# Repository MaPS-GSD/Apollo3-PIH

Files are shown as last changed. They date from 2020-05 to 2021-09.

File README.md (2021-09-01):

# Apollo3-Patient Isolation Hood



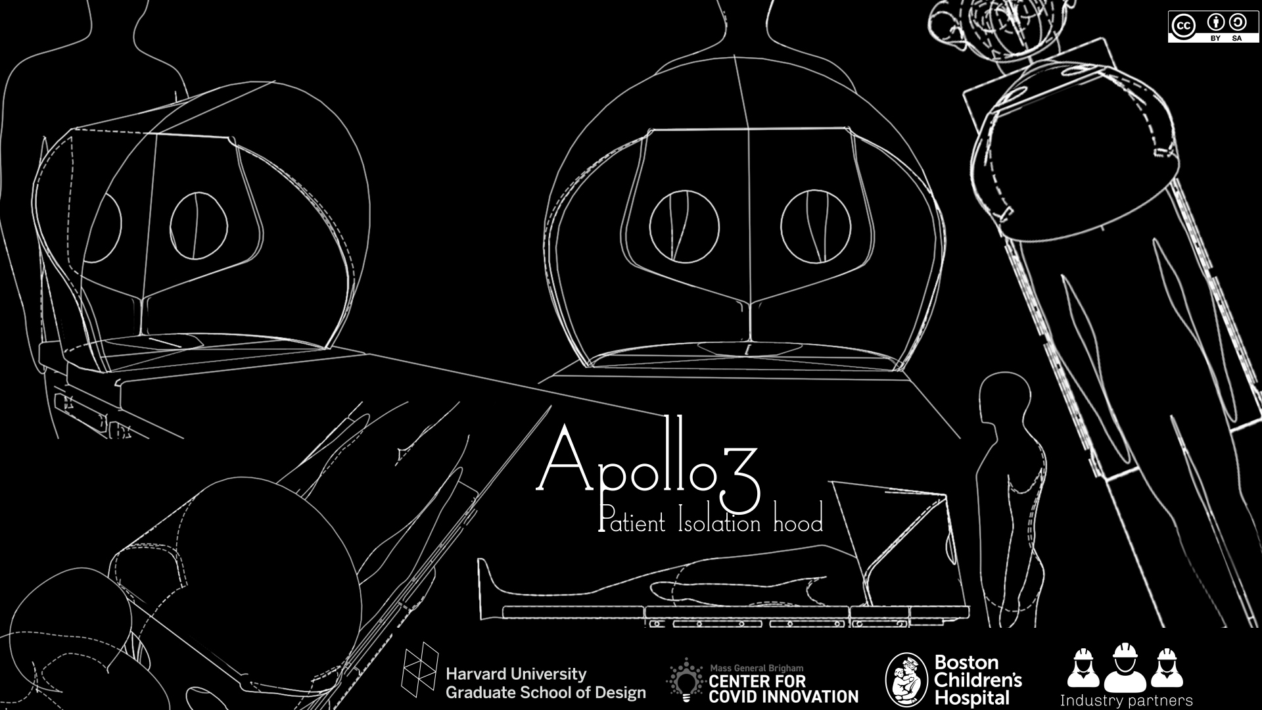
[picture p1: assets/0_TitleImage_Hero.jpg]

## General Information

**Category** : Labware + Devices

**Keywords** :Patient Isolation Hood, PIH, PPE

**Content of Package** :
- Apollo ReadMe (This) [**Print Ready**](README.pdf)
- Apollo3 Vector Cut File (.dxf) - [**Download HERE**](Dxf_cut_files/2020_05_05%20Apollo3_Cut%20File.dxf)
- Apollo Video:  [**Vimeo Link**](https://vimeo.com/415250896)

---
>**For questions, comments, issues and feedback email : [MaP+S Group](mailto:mapsgroup@gsd.harvard.edu?subject=[Apollo3-PIH])**
---

### Disclaimer
Please note: On Friday, May 1 the FDA issued an Emergency Use Authorization for Protective Barrier Enclosures.  The authorization provides specific guidance for manufacturing.  The Apollo PIH has not yet been evaluated with respect to these guidelines.  The letter and two associated fact sheets are available at [https://www.fda.gov/medical-devices/emergency-situations-medical-devices/emergency-use-authorizations#covid19ppe](https://www.fda.gov/medical-devices/emergency-situations-medical-devices/emergency-use-authorizations#covid19ppe).  

The product as a protective barrier enclosure, provides an extra layer of barrier protection in addition to PPE and is not meant to replace PPE.

Please also note: The Apollo PIH is under active development and refinement.  Please check this repository often for design modifications and additional information. 

The Apollo PIH has been tested by clinicians at Massachusetts General Hospital and Boston Children's Hospital, but there are many different regulations regarding medical devices so please follow local guidelines that apply to your region. Please note that safety is the primary objective. Medical equipment must be approved before it is distributed. This is possibly a matter of life or death. 

This work may be reproduced, modified, distributed, performed, and displayed for any purpose, but must acknowledge the Apollo PIH project. Copyright is retained and must be preserved. The work is provided as is; no warranty is provided, and users accept all liability.

### License
Except where otherwise noted, content on this project is licensed under a [Creative Commons Attribution-ShareAlike 4.0 International license](https://creativecommons.org/licenses/by-sa/4.0/). See [License](LICENSE.md).
***
## Project Overview

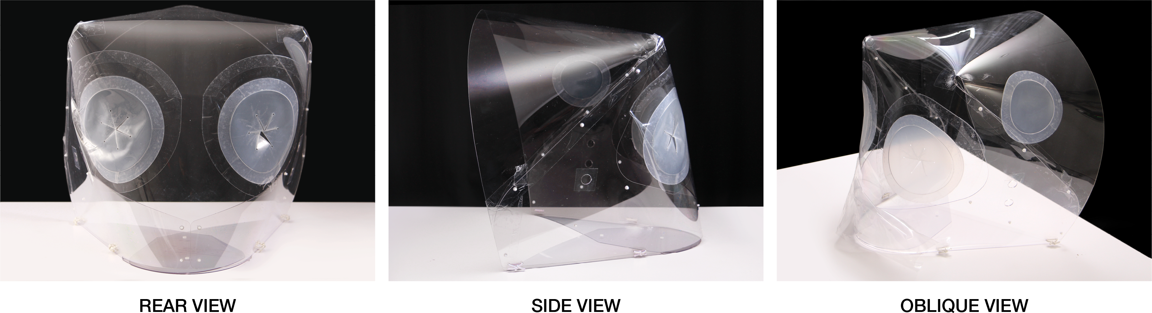
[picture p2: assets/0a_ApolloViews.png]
Apollo3 Patient Isolation Hood
> 

### Description
The Apollo Patient Isolation Hood (PIH) is a localized negative-pressure ventilation system for hospital beds to help contain the droplet spread of COVID-19, including during aerosol-generating medical procedures such as intubation and extubation. The PIH encloses a patient’s upper torso and head in a negative-pressure environment. It provides barrier protection between healthcare provider (HCP) and patient, and aerosol control via the negative pressure environment. The hood may also contain the spread of the virus from less critically-ill patients, reducing the need for invasive procedures.

The versatility of the Apollo PIH means that it can be used in any care setting (OR, PACU, ICU, ED, EMS) and can be rapidly secured to a variety of beds.  The lightweight (<5 lbs) design allows for ease of assembly, use, and disposal. The primary structure is composed of a single flat sheet of PETG plastic that is assembled into a 3-dimensional form, minimizing the number of seams for optimal viewing clarity.  Flexible sealed armports provide HCP access to patients.  A minimal amount of folds and seams in the primary enclosure provide optimal viewing clarity.  

### Design Concept
The primary design goal of the hood was to enclose the patient’s torso and head without restricting HCP ability to provide care or inducing claustrophobia in patients. The enclosure of the Apollo PIH derives its form and rigidity through the principle of active bending, a structural behavior achieved by the elastic deformation of initially flat elements. The main intention was to leverage this structural principle to create a stable, rapidly deployable 3D form that can be fabricated from readily available sheet materials using minimal joinery.

### Key Features
The primary design element of the Apollo PIH is the enclosure - a thin sheet of clear PET-G plastic in 60mil (approximately 1/16”) thickness.  The enclosure can be CNC cut from a flat sheet of PET-G  measuring a minimum of 48” x 72”.  The Apollo PIH enclosure measures approximately 22” in width, 23” in height and 22” in depth and is approximately 0.15 m3 in volume.

> Apollo3 Patient Isolation Hood

Several key features of the prototype are outlined below:
- (2) arm ports at the rear of the PIH provide healthcare provider (HCP) access to the patient. - An additional auxiliary port on one side of the PIH allows for additional patient access as needed.
- Minimal surface seams allow for an unobstructed view of patient.
- Adaptable attachment mechanism allows for use on a variety of bed types (OR, ICU, etc.)
- Side arms provide a double thickness at the base of the PIH for stability and structure
- Various suction ports accept common negative pressure hoses, including a ⅞” diameter (common in OR) as well as smaller 3/16” ID tubing (common in the ICU).  
***
 ### Flow and Pressure Testing - 👨‍⚕MGB
  Work in Progress
  Negative Pressure Hood Working:-  [YouTube Link](https://youtu.be/yTqlieDpH2M)
  ***

## Production Details
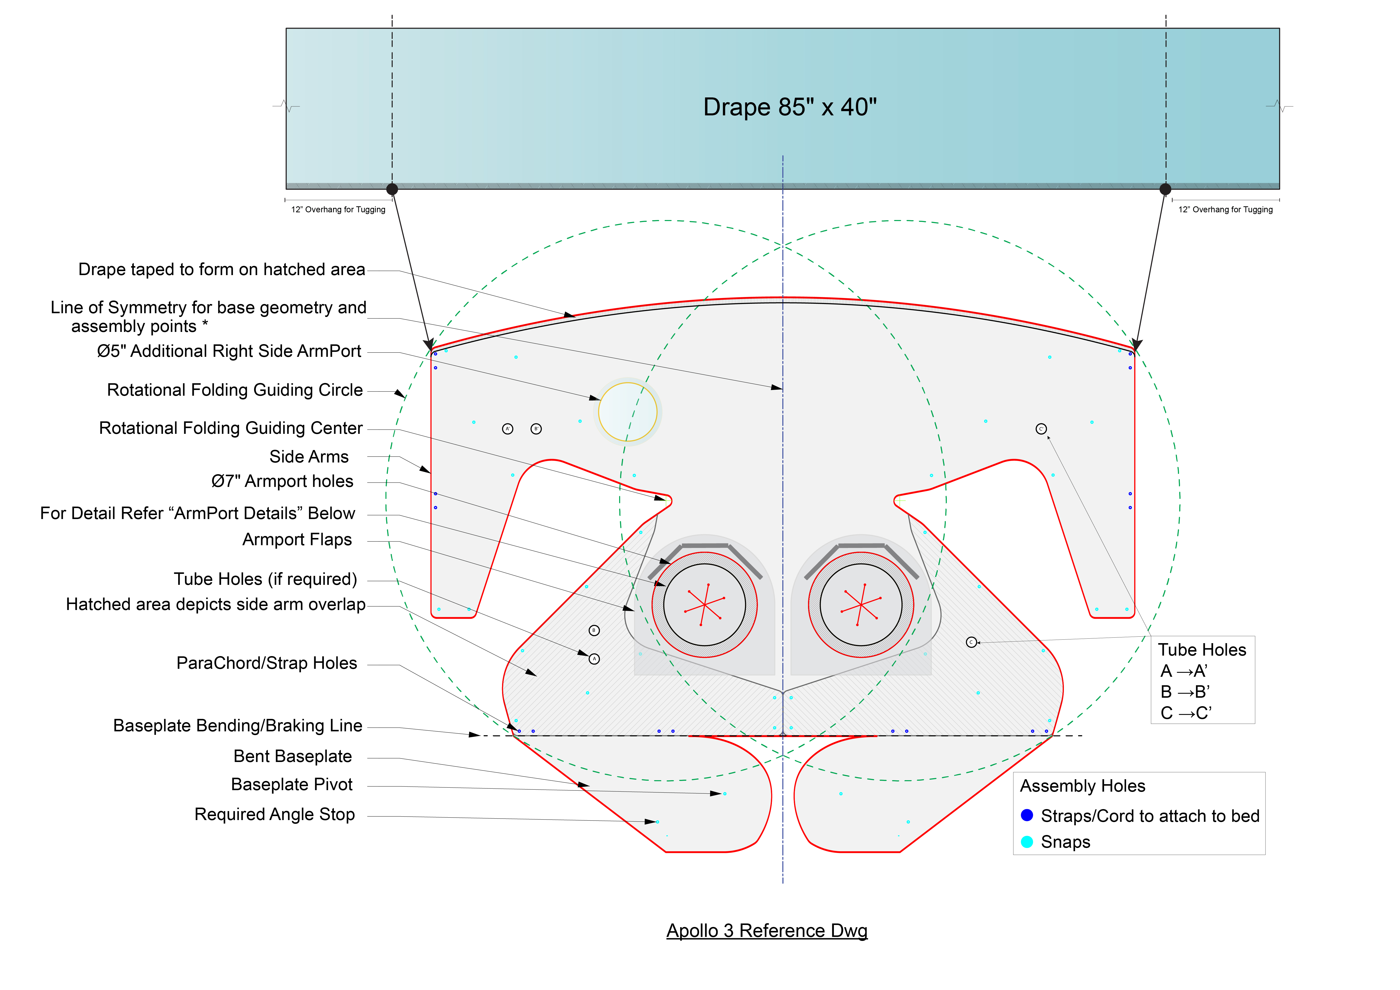
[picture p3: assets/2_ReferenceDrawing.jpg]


### Bill of Materials

Item Description  | Dimensions( in or sqrIn) | Quantity | Link | Notes
|------------- | ------ | -------------| -------------| -------------|
 3/16" bungee cord | 12" | 2 |[Amazon](https://www.amazon.com/T-W-Evans-Cordage-SC-316-100-100-Feet/dp/B00DKA4VQG/ref=sr_1_3?dchild=1&keywords=white+bungee+cord+3%2F16%22&qid=1587383739&s=sporting-goods&sr=1-3-catcorr)
 Velcro cord management strap  | n/a | 2 | [Amazon](https://www.amazon.com/Pasow-Reusable-Fastening-Adjustable-Management/dp/B01CFKQYAW/ref=sr_1_4?dchild=1&keywords=cord+management+velcro+white&qid=1587394037&sr=8-4)
 Adjustment Hook  | n/a | 2 | [Amazon](https://www.homedepot.com/p/ProGrip-Better-Than-Bungee-6-ft-100-lbs-Break-Strength-Particle-Rope-Lock-Paracord-055160/206957471?modalType=drawer)
 Push-In Rivet  | n/a | 17 | [McMaster-Carr](https://www.mcmaster.com/90136a574)
 Button Snaps  | n/a | 1 |  [McMaster-Carr](https://www.mcmaster.com/95691a660) | *1*
 Drape tape / seam tape (must be low surface energy tape)  | 61" | 1 | [HomeDepot](https://www.homedepot.com/p/Gorilla-1-5-in-x-5-yds-Crystal-Clear-Tape-5-Pack-6015002/205493971?mtc=Shopping-B-F_D24-G-D24-Multi-Multi-NA-Feed-PLA-NA-NA-All_Paint&cm_mmc=Shopping-B-F_D24-G-D24-Multi-Multi-NA-Feed-PLA-NA-NA-All_Paint-71700000032325895-58700003835893718-92700030694006321&gclid=CjwKCAjwkPX0BRBKEiwA7THxiJXWI0-JAcbqYryMsjvaev1nBxPw_FWMW1czSJxp9qHvZyLyDKl_yhoCxfgQAvD_BwE&gclsrc=aw.ds) | *2*
 LDPE film (2mil)  | 40" | 1 | [Uline](https://www.uline.com/Product/Detail/S-5445/Plastic-Sheeting/Clear-Poly-Sheeting-2-Mil-8-x-200) 
 1/16" PET-G sheet | 72x48" | 1 | n/a
 Tpu film for port holes (2-5mil)  | 13" X 13"| 2 | n/a
 Tpu film for port hole flaps (2-5mil) | 13" x 13" | 2 | n/a
 Adhesive sheet for attaching handports | 13" x 13" | 4 | [Laminator.com](https://www.laminator.com/51-x-150ft-optically-clear-double-sided-mounting-adhesive-permanent-permanent.html)
 Colored vinyl stickers for intuitive assembly and risk warning | n/a | 4 | [Overnightprints.com](https://www.overnightprints.com/stickers)
 95 gallon clear trash bag for disposal | n/a | 1 | [Uline](https://www.uline.com/Product/Detail/S-15540/Trash-Liners-Bags/Uline-Trash-Liners-95-Gallon-25-Mil-Clear?pricode=WB0503&gadtype=pla&id=S-15540&gclid=Cj0KCQjwhZr1BRCLARIsALjRVQOMShqprypOodH6yqqy-GNPSxb2Hep2NU1SgADXMQsUt7F44VXUqlQaAiDwEALw_wcB&gclsrc=aw.ds)
 Instruction Sheet | n/a | 1 
 1 gallon ziploc to hold instructions and cords | n/a 
---
*1. The button snap used for locking the fixing the position of the baseplate can be replaced by a push-in rivet if needed.*

*2. Must be low-surface-energy tape.*

---
### Recommended Production Guidelines

#### A) Enclosure
#### 1. Cutting
The Apollo PIH requires a minimum stock size of 72” x 48”. The stock can be cut using a number of CNC processes including a knife cutter, laser cutter, or router.  In the case of a CNC router, a ⅛” diameter endmill is required to successfully cut small interior features.  A list of suggested cut settings are provided below.  Please keep in mind that these settings are specific to the machines listed and will likely need to be modified for other scenarios. 
- Knife Cutter ([Zund G3M2500](https://www.zund.com/en/cutting-systems/digital-cutting-systems/g3-cutter))
  - Bed Size: 98” x 52”
  - Tool: Universal Cutting Tool (UCT) with [glide shoe](https://shop.zund.us/en-us/products/alle-produkte/cutting-accessories/gliding-shoe))
  - Blade: Type6 blade
  - Depth: 0.02” per pass
  - Speed : 6” per second 
  - Total Time : ~ 18 minutes.
- Laser Cutter (*450 Watt Multicam Magnus 48x96 CNC Laser, 4” Focal Lens*)
  - Speed: 480 IPM
  - Power 60%
  - Frequency: 10,000 PPI

#### 2. Base-Plate Braking/Bending
 
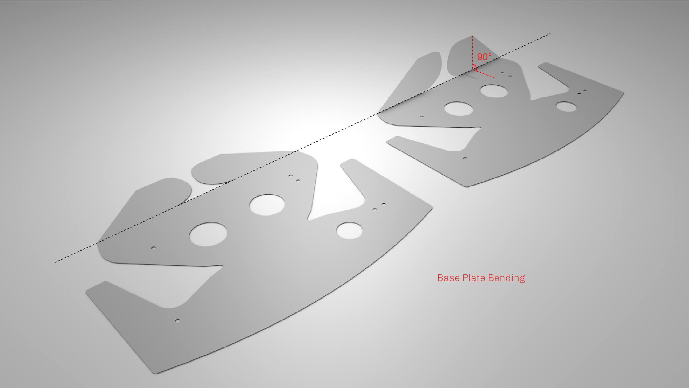
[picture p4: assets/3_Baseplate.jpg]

*Caution : Do not score the material before bending/braking* 

The baseplate portion of the Apollo PIH enclosure must be cold-formed to a 90 degree angle relative to the rest of the enclosure prior to assembly.  To date, this has been successfully accomplished on a sheet metal finger brake such as the Baileigh SBR-4020 shear brake roll ([Link](https://www.baileigh.com/shear-brake-roll-sbr-4020)).
Additional forming processes such as the use of a line brake or heat gun, or design modifications to the enclosure such as eliminating the base plate or incorporating a secondary hinge mechanism, exist as potential alternatives though they have not been tested by the design team. 

#### 3. Push-in Rivets
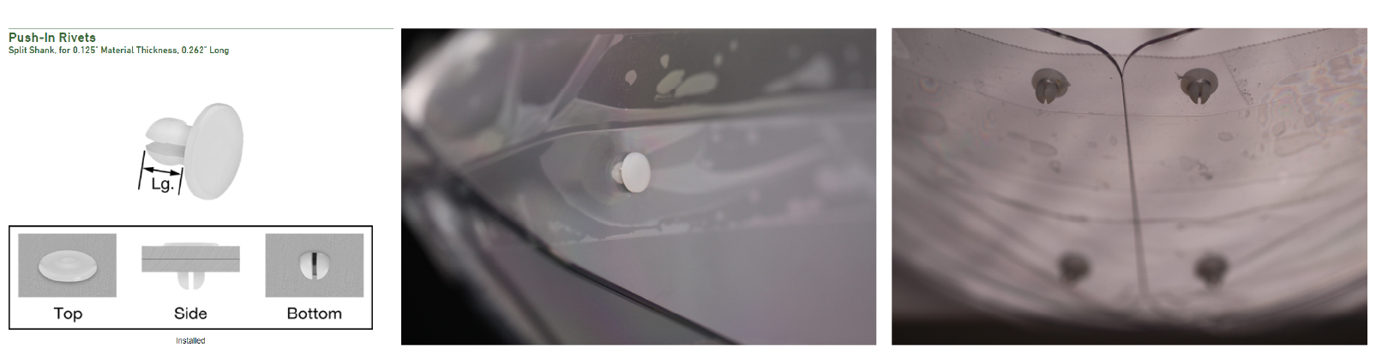
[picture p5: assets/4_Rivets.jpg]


Push-in plastic rivets were selected as the preferred fastener, as they were simple to use and had no sharp edges that could catch on to clothing, medical instruments etc. 3/16” holes in the main enclosure facilitate the riveting and was done by hand. 16 rivets are needed (8 per side of symmetry) for maintaining the shape of the Apollo while 2 rivets (or 1 rivet & a button snap)are needed for the baseplate ( 1 to pivot (*red*) and 1 to lock (*blue*)).
<p align="center">
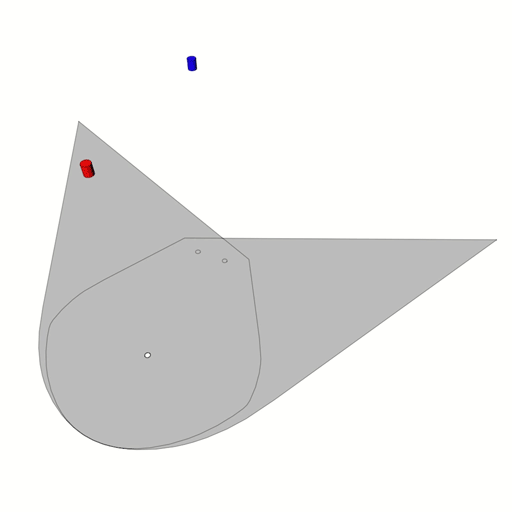
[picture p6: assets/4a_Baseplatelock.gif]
  
</p>

*The width of the Apollo can be adjusted by adjusting the location of the pivot and the lock.Multiple perforations can be added to have it adapt to a range of widths.*

#### B) ArmPorts + Auxiliary Ports

 <p align="center">
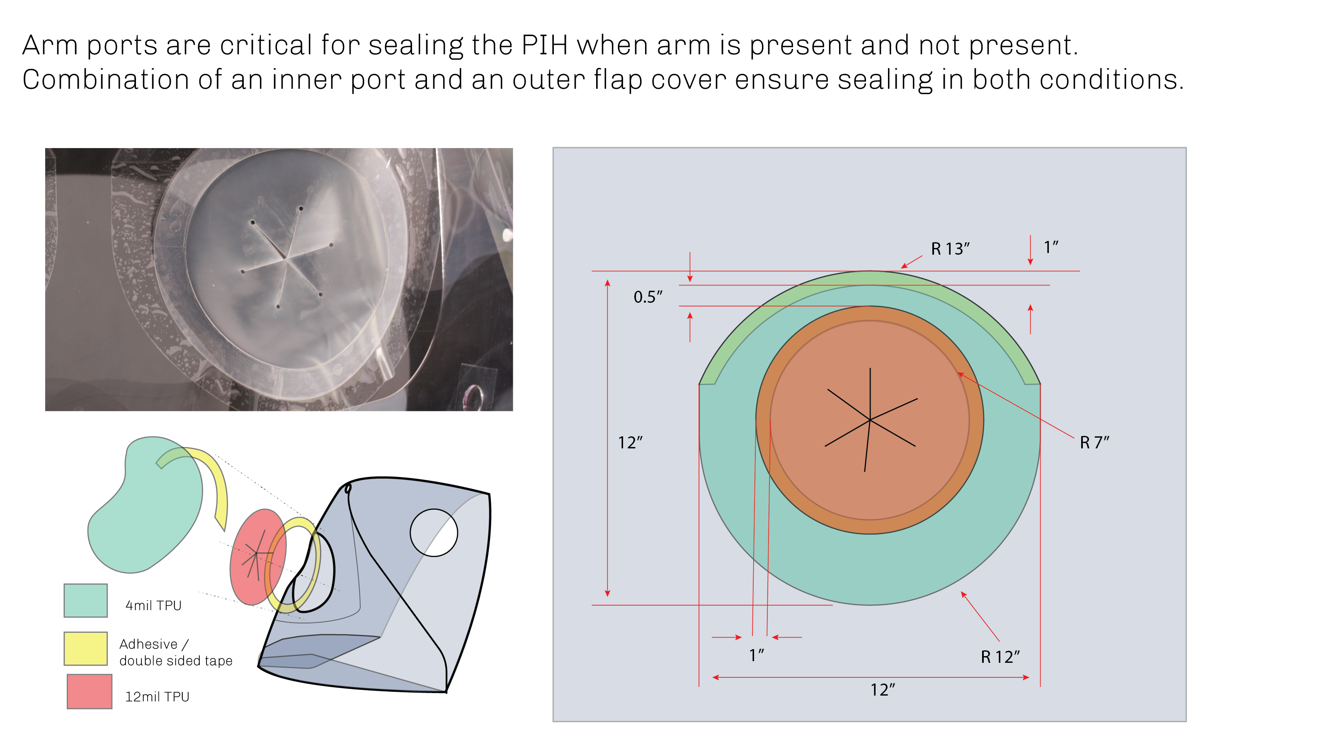
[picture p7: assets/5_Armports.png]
  
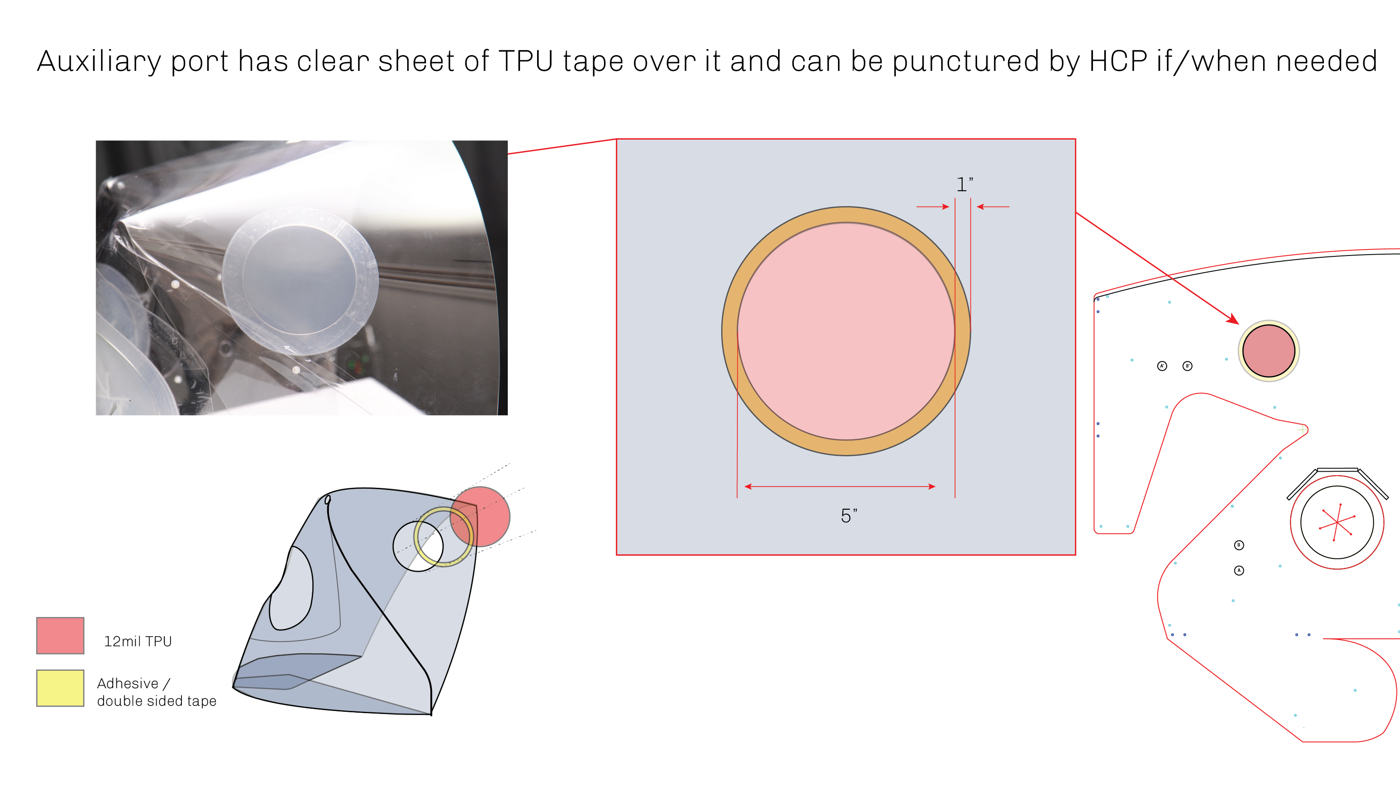
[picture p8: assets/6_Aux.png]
  
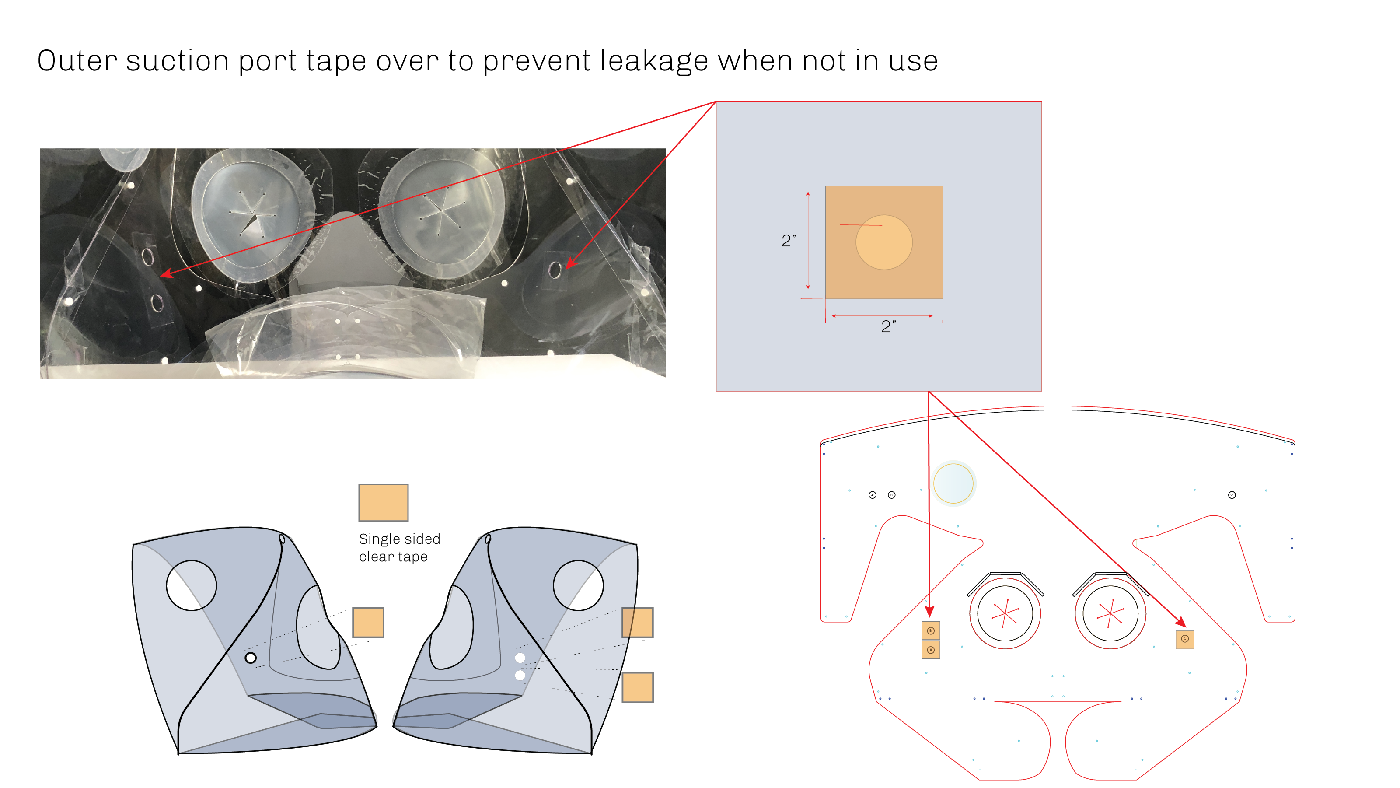
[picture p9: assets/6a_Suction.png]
  
</p>

Each arm and auxiliary port on the Apollo PIH is composed of three primary components - a laser-cut 5 mil TPU portal, a clear, double-sided adhesive film, and a port cover.  

- TPU Portal: Laser cut from 5 mil TPU.  The portal is an inverted “mercedes” design, with circular relief holes at the tip of each cut to minimize the potential for tearing.  It can be CNC cut on a laser cutter or a knife cutting machine such as a ZUND.
- Adhesive Ring: The adhesive ring can be cut from a sheet of adhesive film.  
- The port cover/flap 

#### C) Bed attachment mechanism
<p align="center">
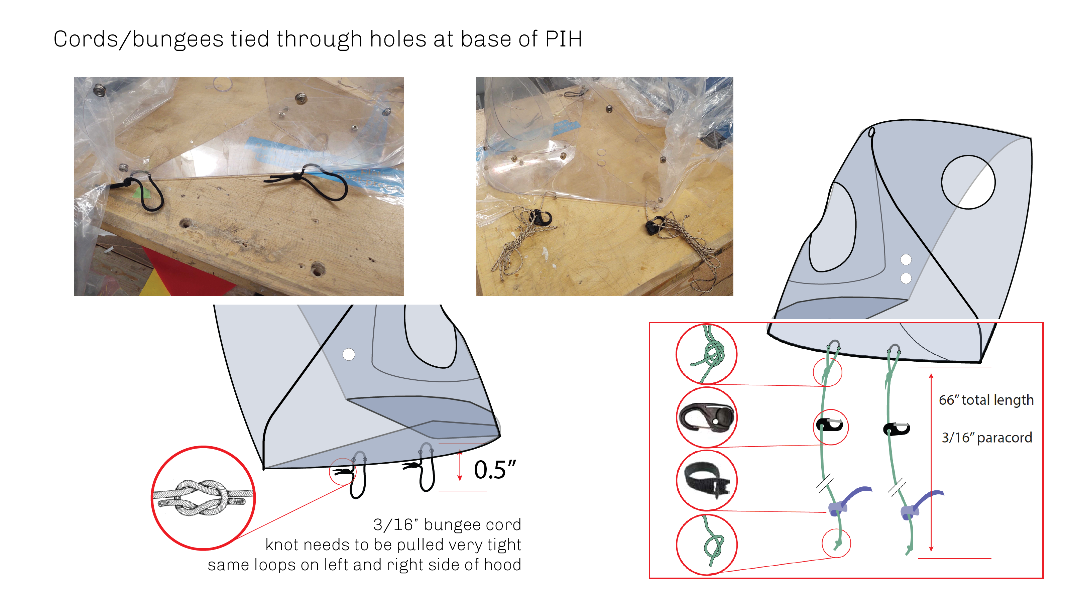
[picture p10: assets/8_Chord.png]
  
</p>

Perforations are located on the base perimeter (dark blue in _Reference drawing_) of the back plate to enable the use of cords/straps in order to attach the Apollo to different sized beds.

#### D) Drape
<p align="center">
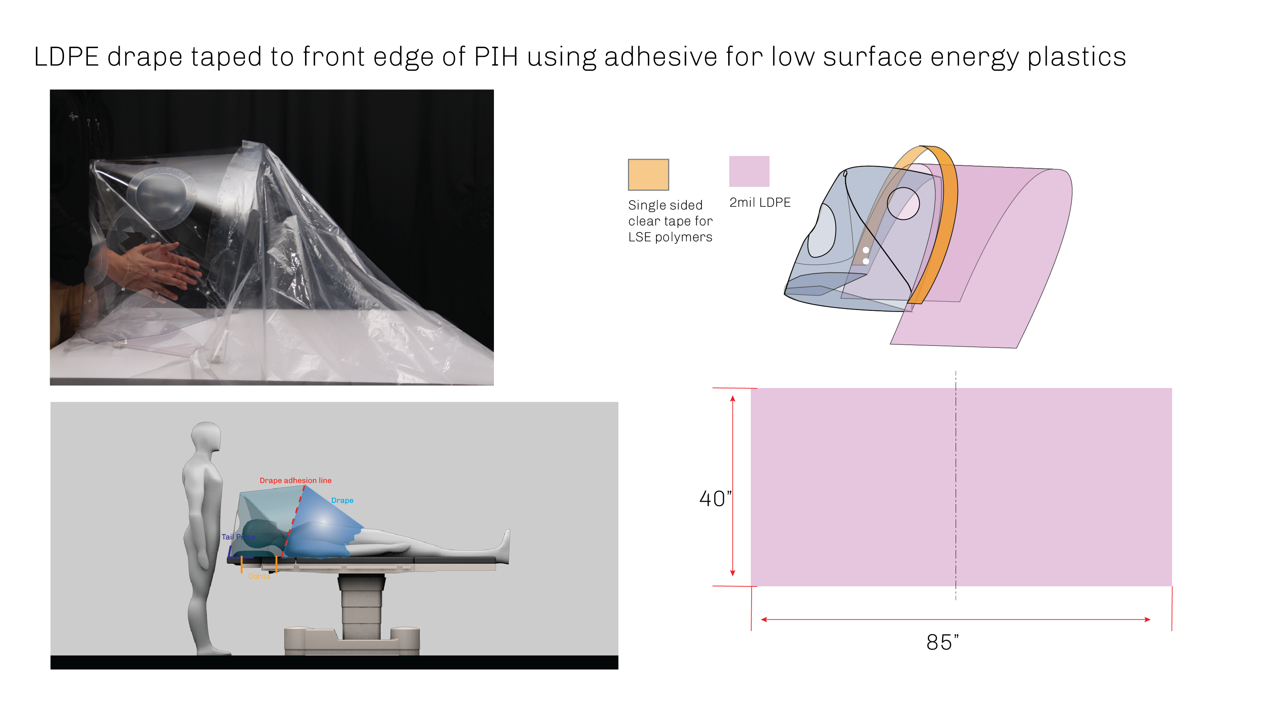
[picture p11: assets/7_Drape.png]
  
</p>

The drape is a rectangular piece of LDPE with dimensions 85” x 40” . Refer to the reference drawing and assembly instructions for details. A 12” offset has been left on both ends to facilitate tucking under the patient to get a good seal. 

#### E) Tail Piece
<p align="center">
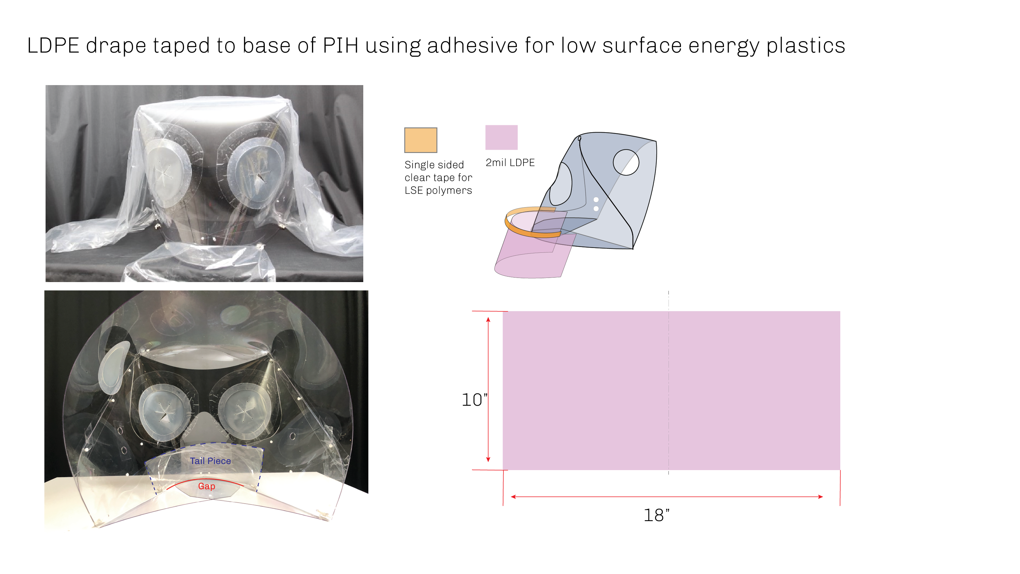
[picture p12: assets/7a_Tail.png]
  
</p> 
A small sheet of LDPE (Same as Drape) is stuck on the back plate and tucked under the baseplate to cover the gap between the baseplate and the back wall to maintain the seal.

### Assembly
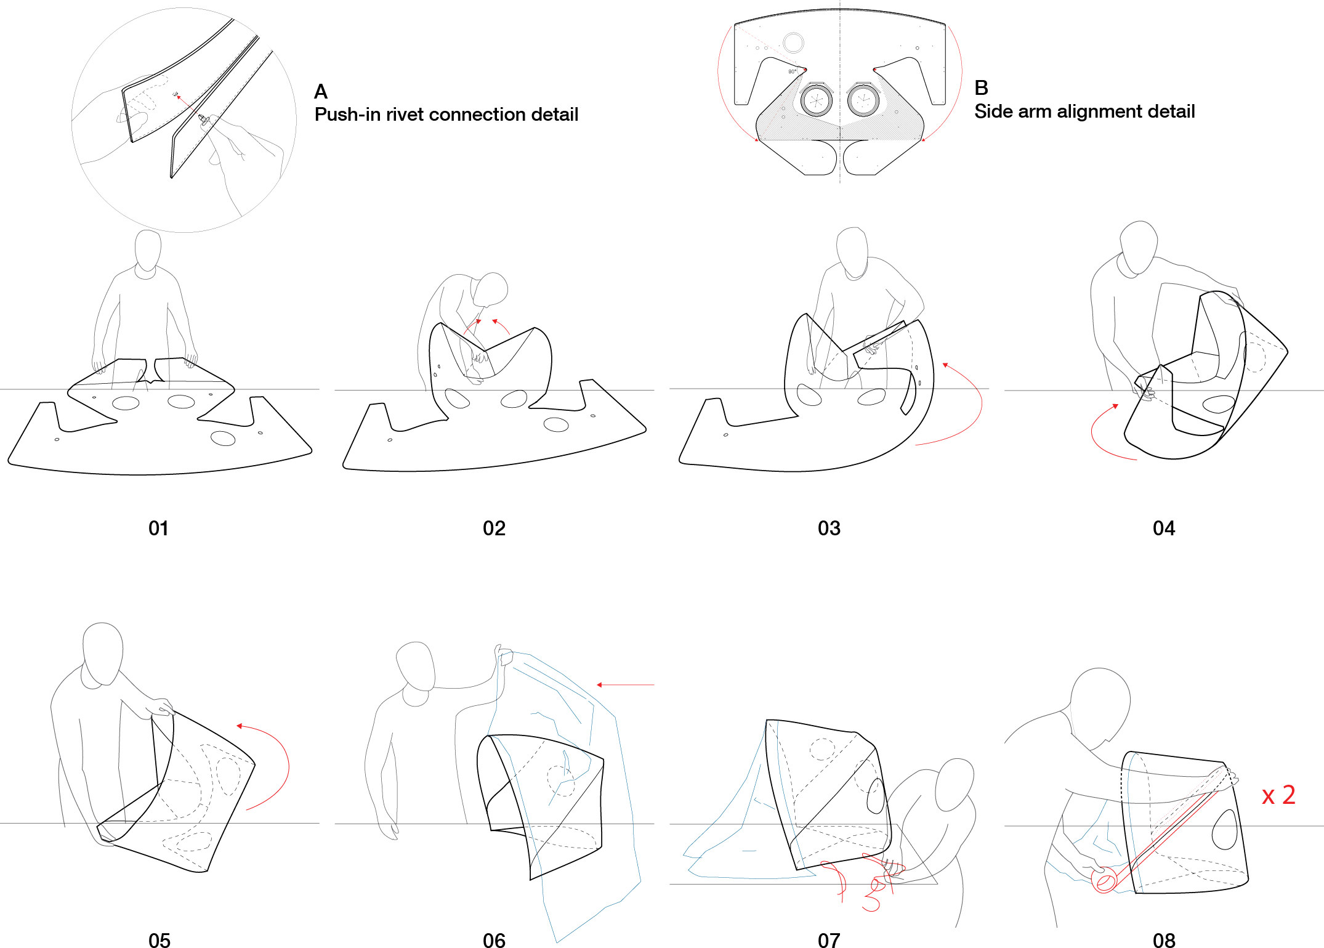
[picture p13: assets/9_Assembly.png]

> 
- Step 01: Place Apollo PIH enclosure on a flat surface with the folded baseplate facing upwards.  
- Step 02: Fasten the opposing sides of the baseplate together using two push-in rivets located on the baseplate.  See detail A for connection detail.  
- Step 03: Fold one side arm toward the interior of the enclosure.  Fasten to the main portion of the enclosure using (8) push-in rivets. 
- Step 04: Repeat Step 03 for the opposite side arm.
- Step 05: Place the Apollo PIH upright so that the baseplate is resting on a horizontal surface. 
- Step 06: Attach the plastic drape to the front edge of the Apollo PIH using double-sided tape.
- Step 07: Fasten the provided straps to one side of the Apollo PIH.
- Step 08: Adhere clear tape over the external seams of the Apollo PIH (one per side), taking care to completely cover the seam. 

### Alternate Details
Below are some alternative details we have experimented with towards the end goal as design variants but these are yet to be tested clinically.

- **Material**

    While the Apollo PIH is designed to be fabricated from PET-G measuring 60mil (~1/16”) in thickness, though early prototypes fabricated from thinner, 30mil (~1/32”) were also sufficiently rigid. 

- **Form**

    Following alternatives have not been checked thoroughly in a clinical setting  and have only been provided as suggestions.

  - Apollo 1 Main Feature:
    - Use of Tabs and Slots instead of hardware
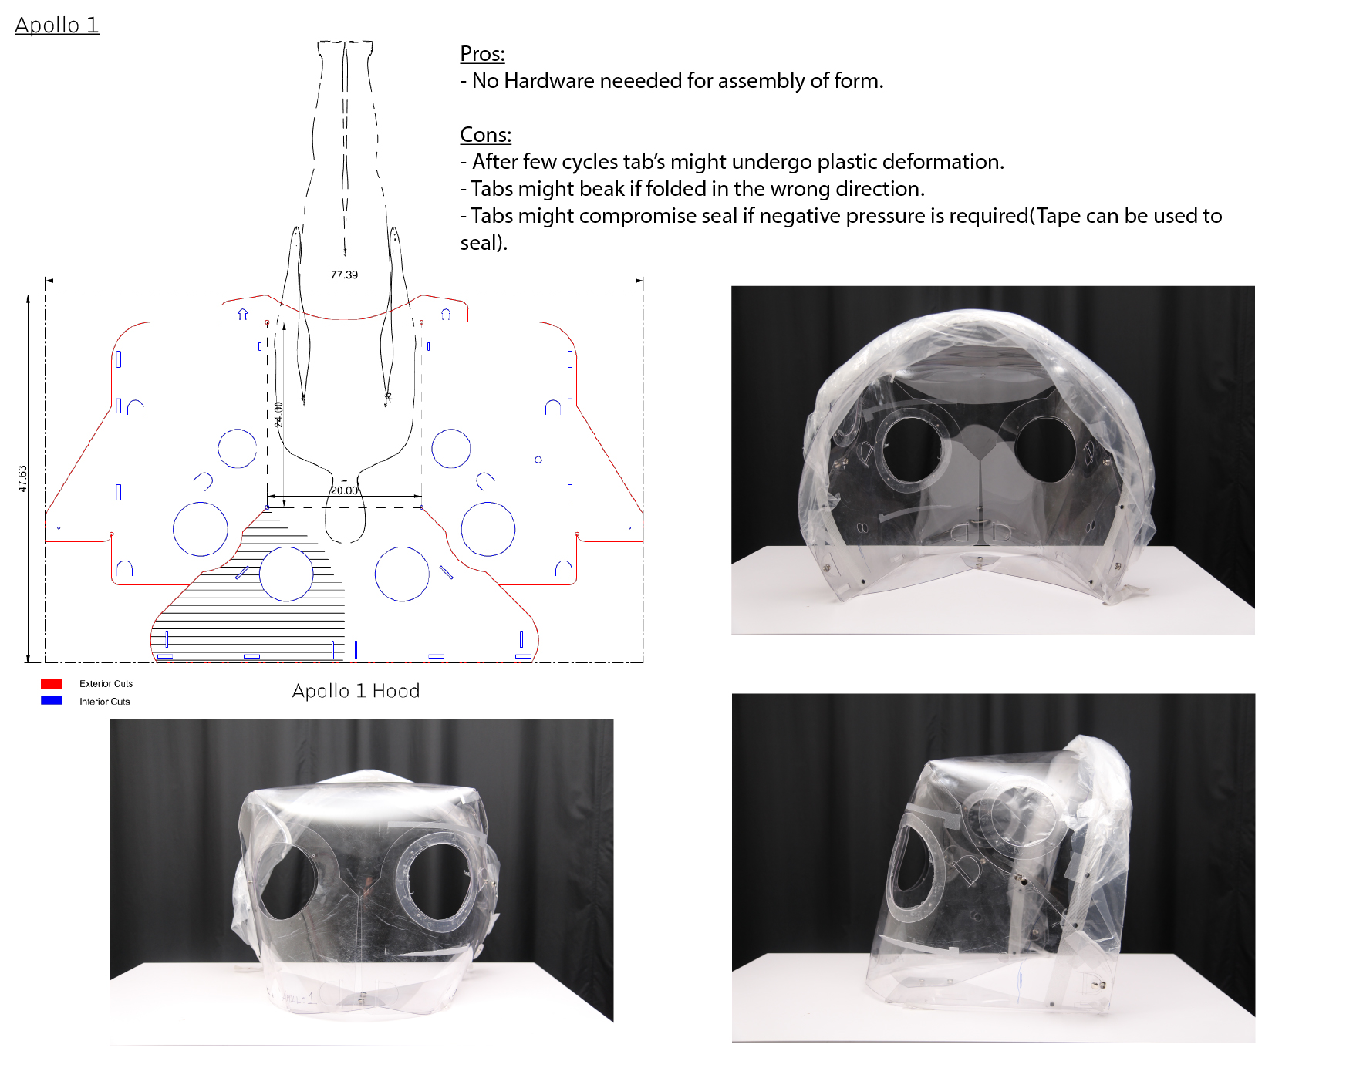
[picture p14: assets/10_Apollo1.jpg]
Apollo3 Patient Isolation Hood
    

  - Apollo 1.5_Minimal Main Feature:
    - Reduction of overlap and material.
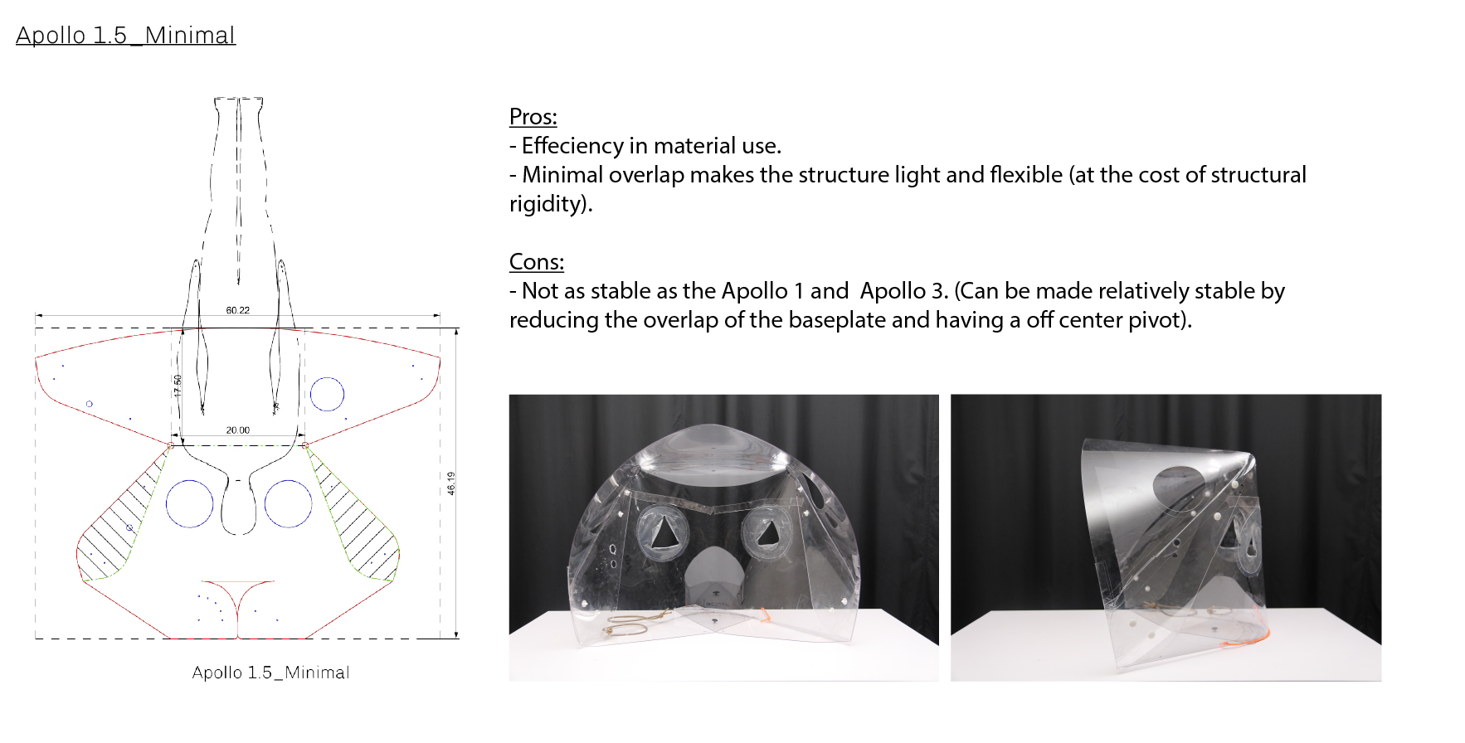
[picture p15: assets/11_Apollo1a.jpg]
Apollo3 Patient Isolation Hood
    

- **Arm Ports**
 
    <p align="center">
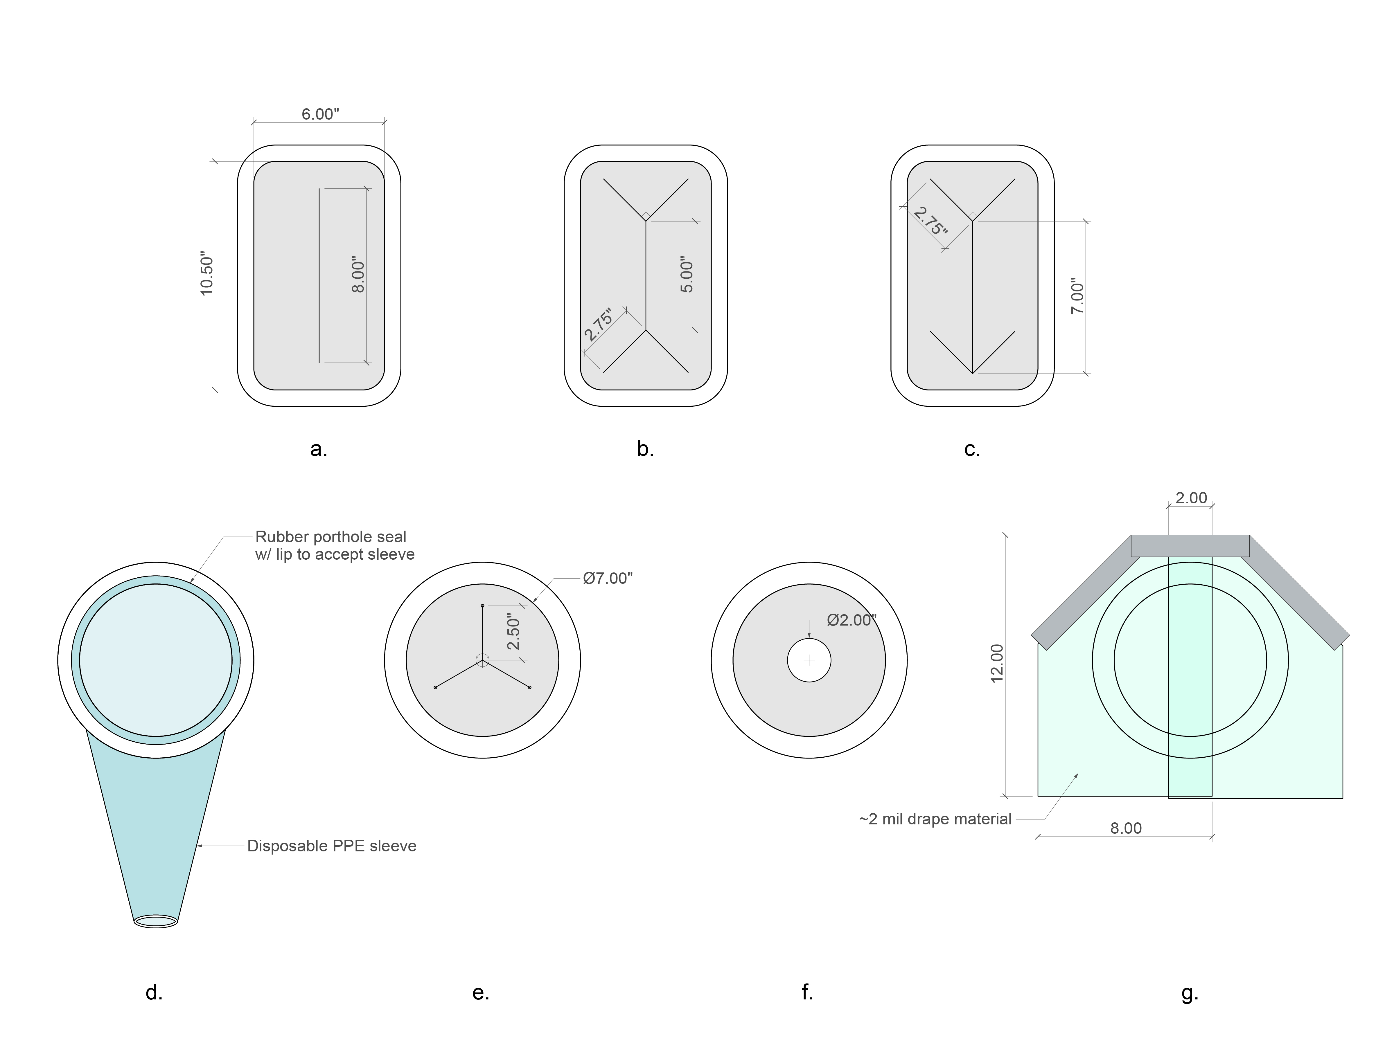
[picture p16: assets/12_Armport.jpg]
    
    </p>

Multiple iterations of the armport design were undertaken with various materials and can be found in the diagram above. 
- Versions a and f Require a thinner gauge or extensible material as they can otherwise restrict arm movements while in use. Version f also requires a secondary drape taped over the opening to maintain a seal
- Versions b, c, and e work well with the specified 5+mil TPU and 1/16” silicone sheets (available on McMaster Carr). They feature a self-closing design and when used with the silicone sheets may not require a covering drape. Version c is best for thinner materials that lack the stiffness to hold their shape overwise
- Version d makes use of disposable PPE sleeves widely available in many material types. The sleeve is stretched around a rubber porthole seal (such as [this product).
- Version g simply uses two pieces of the drape material with an overlap to help limit air escape when in use.
- Clear PVC sheets were experimented with in both 0.08” and 0.04” thicknesses but were found to be too stiff to work properly and often grabbed at the sleeves and gloves when in use. 

## Documentation
>Evolution
<p align="center">
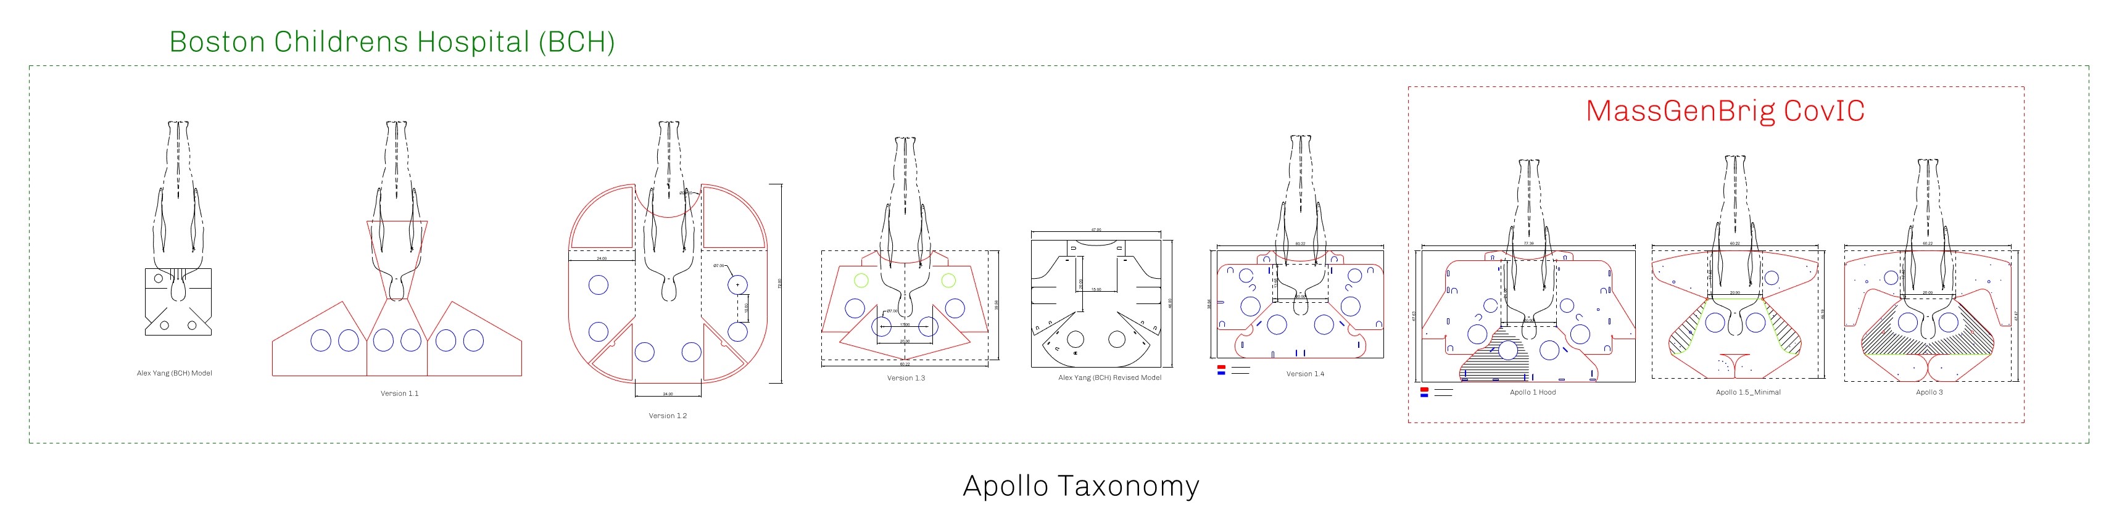
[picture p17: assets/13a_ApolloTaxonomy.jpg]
    
    </p>
    
>Apollo3
<p align="center">
    
    </p>

>Apollo3 Clinical Testing
<p align="center">
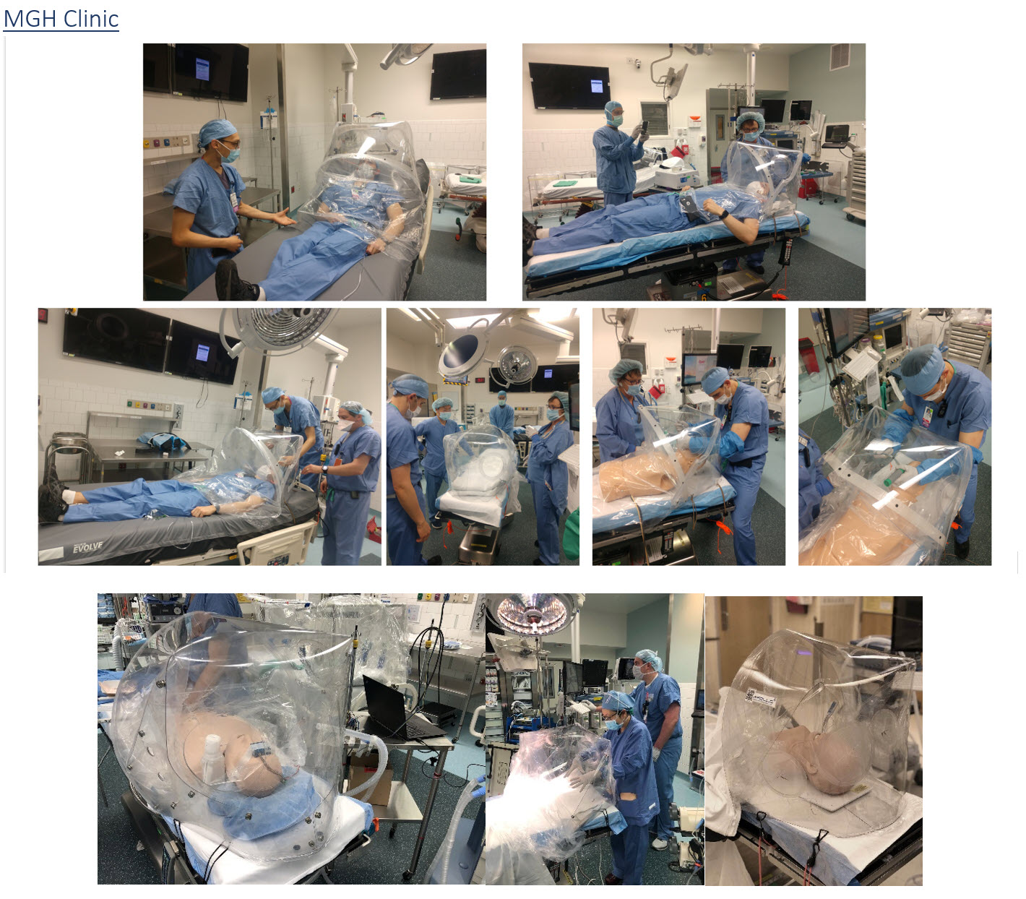
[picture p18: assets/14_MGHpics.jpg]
    
    </p>

## Update - 2021_08_31 - Apollo 4 - Production Model by Nathan Phipps
- Description:
Apollo 4 includes several modifications for manufacturing efficiencies as well as continued requests from clinicians. Clinical updates include an extra set of hand ports for accessing patients, removal of the TPU auxiliary port located on the upper right (clinicians view) of the unit, and addition of elliptical suction ports to allow for cylindrical suction tubes entering at a steep angle into the hood. The main alteration for manufacturability was modified PETG body shape which could allow for two units to be cut out of a single 4'x8' sheet, thus increasing yield in production. This new shape was created by removing the "wings", which offered increased stability and stiffness and instead broadening the base of the unit to increase stability. Apollo Medical Solutions, a company started by Nate Phipps and Chris Tolles was formed to facilitate production and distribution of the Apollo 4; the device was produced by H. Loeb Corporation of New Bedford, MA and purchased for testing by Massachusetts General Hospital. 

- Apollo4  Assembly Instructions [**Print Ready**](apollo3_productionModel_instructionsForAssembly.pdf)
- Apollo4 Vector Cut File (.dxf) - [**Download HERE**](apollo3_productionModel_mainBody_twoPer4x8Sheet.dxf)
- Apollo4 BOQ (.xlsx) - [**Download HERE**](apollo3_productionModel_BOM.xlsx)

<p float="left">

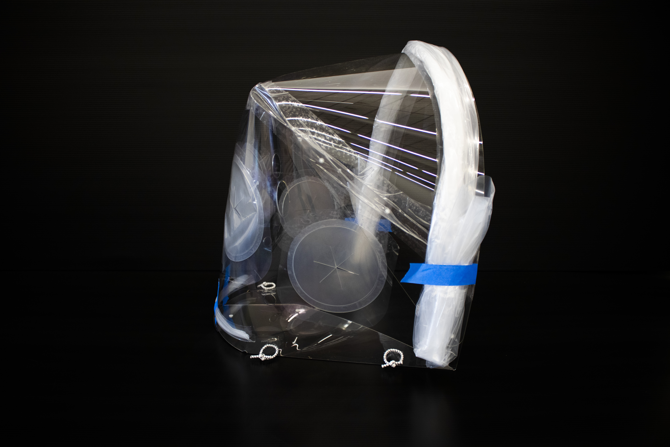
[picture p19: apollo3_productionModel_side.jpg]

</p>
<p float="left">

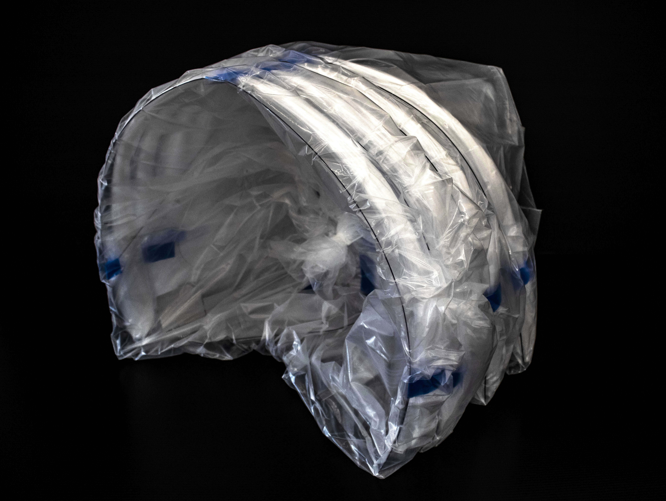
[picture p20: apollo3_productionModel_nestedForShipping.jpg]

</p>
<p float="left">
  
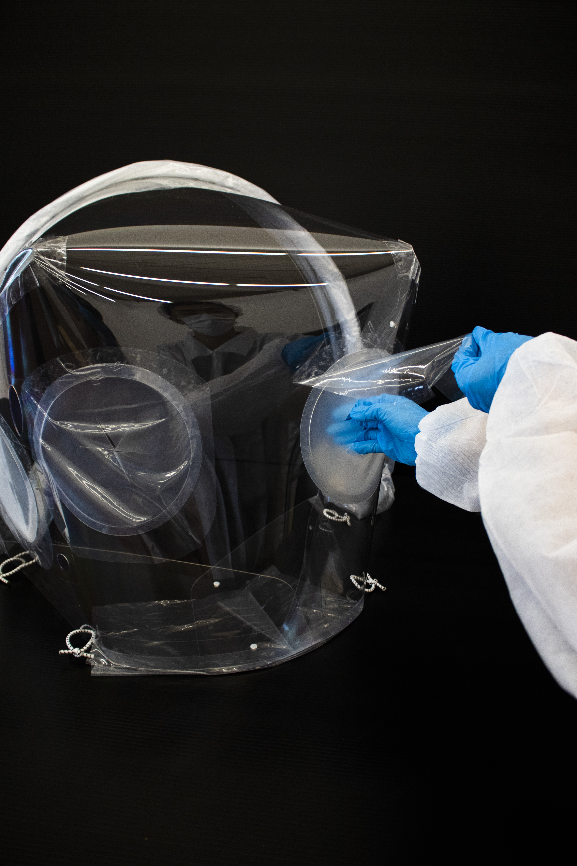
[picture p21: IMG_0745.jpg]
   
</p>
<p float="left">
  
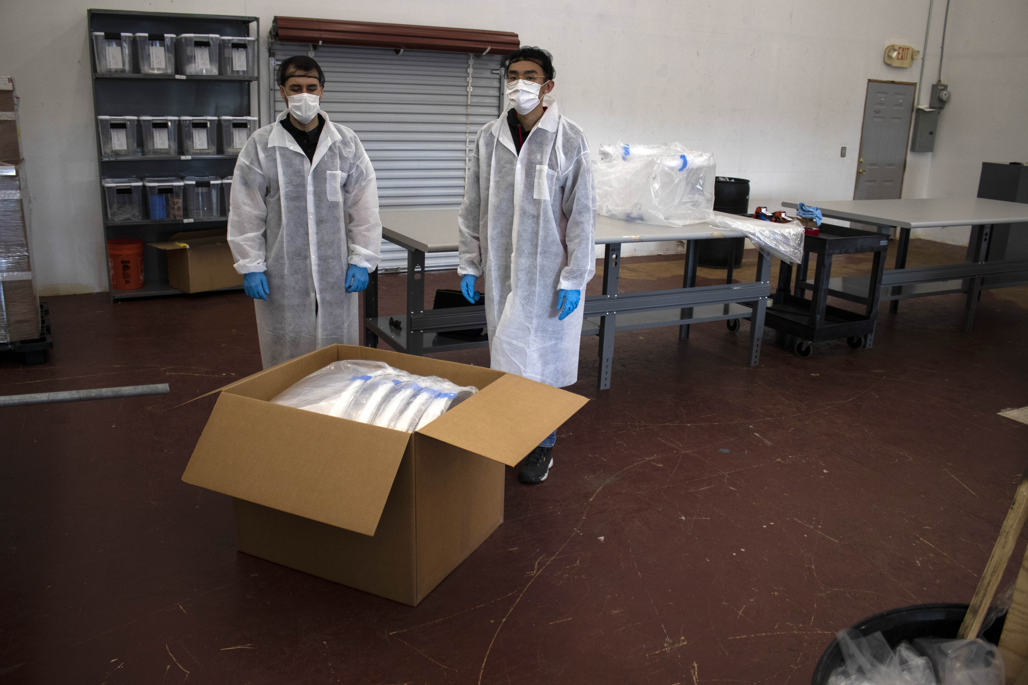
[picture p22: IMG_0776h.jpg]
   
</p>

## Attribution 

Attribution Report 
- **PIH Dimensions:** 
MGB Group + Boston Children’s Hospital
- **Form/Concept:**
Saurabh Mhatre, Christopher Hansen, Nathan Phipps, Eric Howeler, Samuel Smith, MD, 
- **Arm Ports
Design:** Daniel Tish, Daniel Castello, Christopher Hansen, Jonathan Grinham, 
- **Clinical Input:** Samuel Smith, MD; 
- **Base Structure/Attachment Mechanism:**
Nathan Phipps, 
- **Drape:**
Nathan Phipps, Chris Hansen, 

## Acknowledgements
- Several clinicians provided key clinical feedback that drove design decisions, from MGH Anesthesia: Samuel Smith, MD, MPH; JP Wang, MD, PhD; Michelle Szabo, MD; Scott Streckenbach, MD; Alex Kuo, MD; Kendrick Shaw, MD, PhD; Angela Dai; Matt Vanneman, MD; Celeste Day.  From MGH Pediatrics, Kris Olson.  From the MGB Center for COVID Innovation; Li Li, PhD; Aditya Kumar; and Gary Tearney, MD, PHD.  
- Chris Hansen, Digital Fabrication Technical Specialist at the Harvard GSD;  Eric Howeler, Associate Professor of Architecture at the GSD; Saurabh Mhatre, Research Associate at the Harvard GSD & Harvard CGBC; and Nathan Phipps, played key roles in refining, prototyping, and coordinating fabrication of the Apollo 3 design. Zach Seibold, Jonathan Grinham, Daniel Tish, Daniel Castello and Ryan Pierce participated in design iteration and early prototyping.  
- James Weaver, Senior Research Scientist at the Wyss, facilitated the initial collaboration and has been instrumental in sourcing materials. 
- The Boston Children’s Hospital Surgical Innovation Fellowship team, including Heung Bae Kim, MD; Farokh Demehri, MD; Robert Crum, MD; Kyle Wu, MD; Brianna Slatnick, MD; and Alex Yang, BS, helped to develop the first versions of the Apollo design and provided clinical input throughout the design process.
- Initial design prototypes were produced with the help of PolyFab, and Roger Diebold (CEO, Solchroma Technologies) along with H. Loeb Corporation.

A full attribution list is as follows
Aaron Ross,
Adam Smith,
Aditya Kumar,
Alex Kobald,
Alex Yang,
Alexander Kuo,
Angela Dai,
Brianna Slatnick,
Celeste Day,
Chris Hansen,
Chris White,
Daniel Castelo,
Daniel Tish,
David Concha,
David Hamm,
David Wallace,
Eric Howeler,
Euan Mowat,
Farokh Demehri,
Fernanda Sakamoto,
Heung Bae Kim,
James Weaver,
Jonathan Grinham,
Jonathan Langer,
Koushik Garapti,
Kristian Olson,
Kyle Wu,
Lara Tomholt,
Martin Bechthold,
Mehra Golshan,
Michael Sherman,
Michele Szabo,
Norman Wen,
Robert Crum,
Ryan Pierce,
Sam Smith,
Saurabh Mhatre,
Ted Ngai,
Ted Sirota,
Zach Seibold.

## References

### Press
- Harvard GSD Press Release [Link](https://www.gsd.harvard.edu/2020/05/gsd-participates-in-global-open-source-effort-to-develop-patient-isolation-hoods-for-boston-hospitals/)
- Selected Articles
    - https://news.harvard.edu/gazette/story/2020/04/graduate-school-of-design-begins-ppe-production-for-area-hospitals/                                                 
    - https://www.architecturalrecord.com/articles/14570-architects-and-engineers-help-develop-isolation-hood-for-covid-19-patients     
    - https://archinect.com/news/article/150193745/harvard-ppe-team-uses-slack-to-design-patient-isolation-hood-for-hospital-use
    - https://www.dezeen.com/2020/04/20/patient-isolation-hood-coronavirus-personal-protective-equipment/            
    - https://www.dezeen.com/2020/04/21/design-input-healthcare-risk/                        
    - https://archpaper.com/2020/04/harvard-gsd-local-hospitals-coronavirus-personal-protective-equipment/  

### Similar Efforts
- [MIT Center for Bits and Atoms](https://gitlab.cba.mit.edu/pub/coronavirus/tracking)
- [Toledo plastic companies](https://www.wtol.com/article/news/health/coronavirus/local-plastic-companies-create-device-for-protecting-healthcare-workers/512-0068d863-82f7-436e-97ea-66212c4a67f8)
- [Care Shield](https://www.wcpo.com/news/coronavirus/cincinnati-doctors-invention-helps-protect-nycs-frontline-health-care-workers-from-covid-19)  
- [Stuck Design](https://www.youtube.com/watch?v=cFtV-cP0PMo)

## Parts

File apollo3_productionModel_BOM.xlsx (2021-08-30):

BOM
Components | Name | Supplier | Supplier Part Number | Qty per Unit
Part 1 | PETG main body | Polymershapes | PETG .060 | 0.5
Part 2 | Rivets | Mcmaster-Carr | 90136A574 | 10
Part 3 | 2’’ Gorilla Tape | Home Depot | #204593167 | 3.5'' x 2 locations 2'' x 2 locations 17'' x 1 location 57'' x 1 location
Part 4 | Adhesive rings for small ports | NOVA FILMS & FOILS | NFS1801 | 2
Part 5 | Adhesive rings for large ports | NOVA FILMS & FOILS | NFS1801 | 2
Part 6 | 12 mil tpu ports small | American Polyfilm | HTM-8501-S, polyether TPU Film | 2
Part 7 | 12 mil tpu ports large | American Polyfilm | HTM-8501-S, polyether TPU Film | 2
Part 8 | 3 mil tpu flaps small | American Polyfilm | MT-1001-C, Polyether Tau Film | 2
Part 9 | 3 mil tpu flaps large | American Polyfilm | MT-1001-C, Polyether Tau Film | 2
Part 10 | Bungee cord | Usa Products group | #055166 | 2
Part 11 | Idpe tail drap | Uline | S-5445 (https://www.uline.com/Product/Detail/S-5445/Plastic-Sheeting/Clear-Poly-Sheeting-2-Mil-8-x-200?FromOrderHistory=Y) | 1
Part 12 | 3’’ packing tape | Uline | S-9736 | 48''
Part 13 | 3m ScotchBlue | Home Depot | #100550611 | 6'' x 5 locations 10'' x 1 location
Part 14 | Idpe main drape | Uline | S-5445 (https://www.uline.com/Product/Detail/S-5445/Plastic-Sheeting/Clear-Poly-Sheeting-2-Mil-8-x-200?FromOrderHistory=Y) | 1
Part 15 | Progrip cord assembly | Home Depot | #206957471 | 2
Part 16 | Velcro ziptie | Uline | S-17101 | 2
Part 17 | 1 gal. Ziploc bag | Uline | S-23779 (https://www.uline.com/Product/Detail/S-23779/Food-Bags/Ziploc-Freezer-Bags-1-Gallon) | 1
Part 18 | Usage info packet | Apollo Medical Solutions | Label Pack 1.0 | 1
Part 19 | Warning and ID label | Staples | 764134 | 1
Part 20 | QR code label | Staples | 764134 | 1
Part 21 | Reusable ziptie | Uline | S-1258NAT (https://www.uline.com/Product/Detail/S-1258NAT/Cable-Ties-and-Tools/Releasable-Nylon-Cable-Ties-5-1-2-Natural?FromOrderHistory=Y) | 1
Part 22 | 95 gal. clear trash bag | Uline | S-15540 (https://www.uline.com/Product/Detail/S-15540/Trash-Liners-Bags/Uline-Trash-Liners-95-Gallon-25-Mil-Clear?FromOrderHistory=Y) | 1

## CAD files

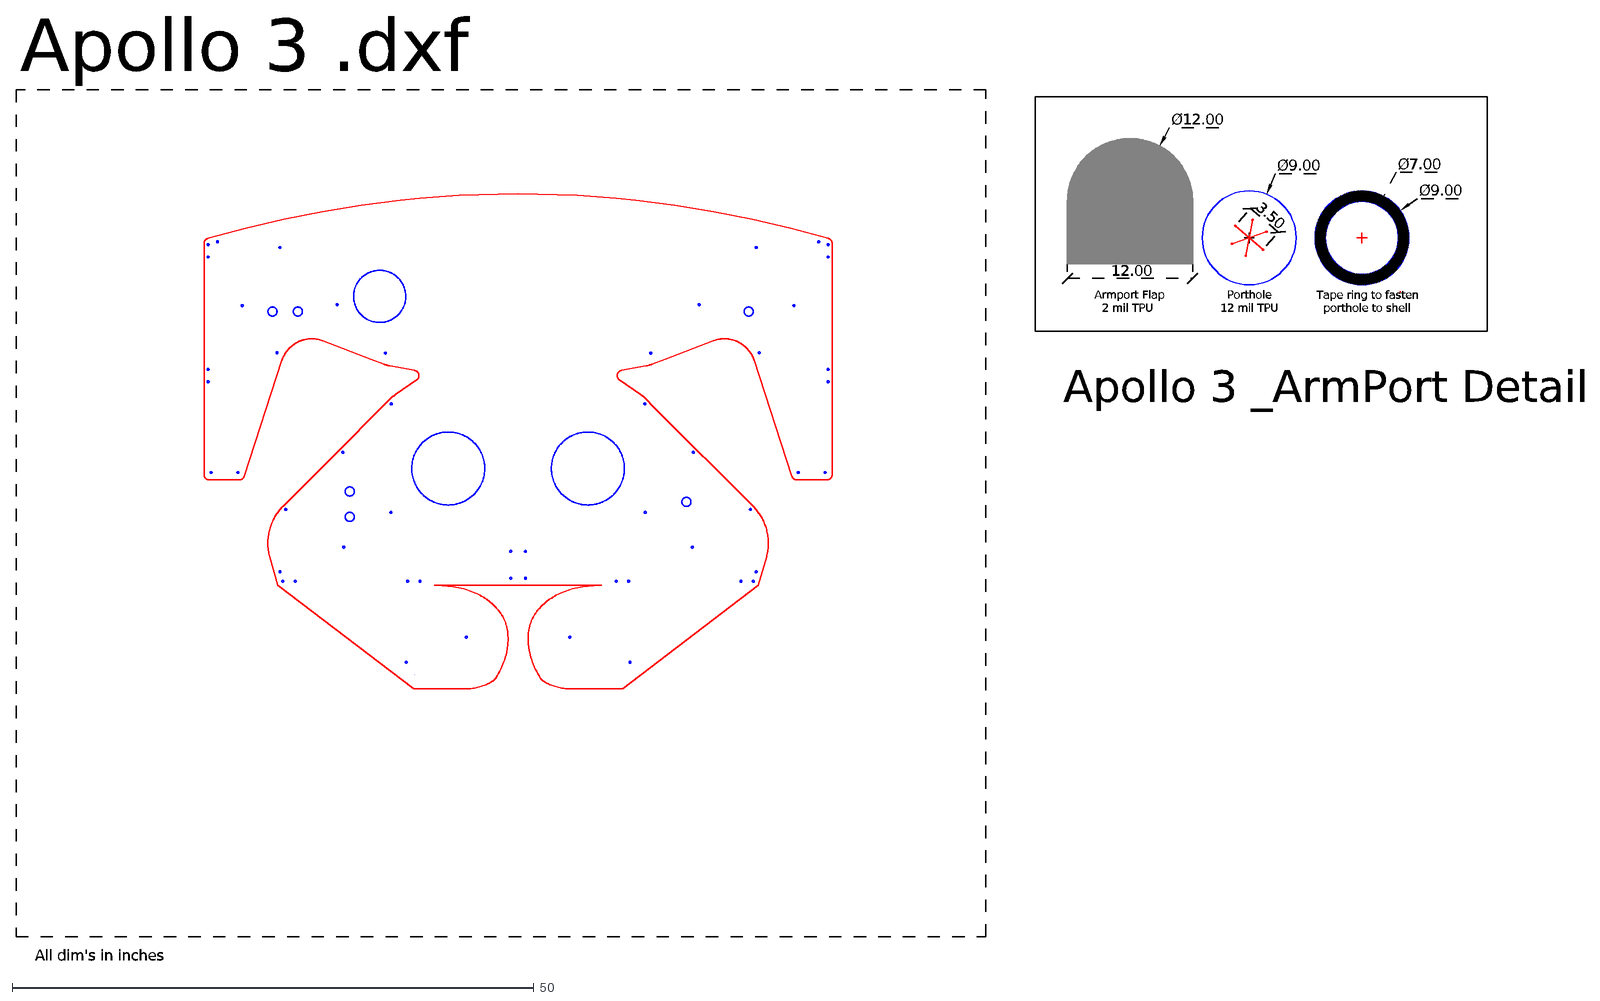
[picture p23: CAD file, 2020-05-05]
Dxf_cut_files/2020_05_05 Apollo3_Cut File.dxf
All dim's in inches
Apollo 3 _ArmPort Detail
Armport Flap
2 mil TPU
12.00
Ø12.00
Tape ring to fasten
porthole to shell
Porthole
12 mil TPU
3.50
Ø9.00
Ø7.00
Apollo 3 .dxf

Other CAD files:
apollo3_productionModel_mainBody_twoPer4x8Sheet.dxf

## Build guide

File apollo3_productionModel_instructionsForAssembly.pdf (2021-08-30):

# SINGLE PATIENT USE

# NOT INTENDED TO REPLACE PPE

# WARNING

Suffocaon Hazard.

### Plasc film can be dangerous. To avoid danger of suffocaon, keep this film

away from the mouth of the paent.

# WARNING

Paent Unaended Hazard.

### Leaving paent unaended can cause harm. A qualified care team member

must accompany paent at all mes.

# WARNING

Fire Risk.

OXYGEN RICH ENVIRONMENT
NO combusitbles inside hood while in use, including hand sanizer or cleaning soluons.

NO ignion sources inside hood, including any electronics, lasers, heat, or light sources.

# Apollo Medical Solutions

Apollo Medical Solutions, 2020
46 Cottage Street, Watertown, MA, 02472 | 1/4

# Instructions, Labels, and Standard Operating Procedure

# APOLLO 4 Patient Isolation Hood

Caution: Federal law restricts this device to sale by or on the order of a licensed healthcare provider.

# REPORTING LANGUAGE

PRODUCT DESCRIPTION:

COMPONENT LIST:

INDICATIONS FOR USE:

INTENDED USE:

THIS PRODUCT IS AUTHORIZED FOR USE BY FDA UNDER AN EMERGENCY USE AUTHORIZATION (EUA) PURSUANT TO SECTION 564(b)(1)(C) OF THE FEDERAL FOOD DRUG AND COSMETIC ACT

THIS PRODUCT IS NOT AN FDA APPROVED MEDICAL DEVICE, USE OF THIS DEVICE IS AUTHORIZED BY THE FDA FOR THE DURATION OF THE EUA AND SHOULD NOT BE USED AFTER THE EUA HAS BEEN CONCLUDED, TERMINATED, OR REVOKED BY THE FDA.

PRIOR TO USE: Health care provider should assess patient for respiratory status and dicult airway prior to use of this device.

PRECAUTIONS:
+If device impedes care of or communication with patient it should be removed immediately following instructions in “Removal of Device” section of this page, below.
+Normal PPE should be used in conjunction with this device. Device not intended to replace PPE.
+The Benets/Risks of using a protective barrier enclosure device for airway management in certain populations should be predeter-mined by the HCP. These populations include but are not limited to:
-Patients requiring emergency endotracheal intubation who have severe respiratory compromise
-Patients with an anticipated or known history of dicult airway
-Patients who are morbidly obese
-Pregnant women in the 2nd or 3rd trimester
-Individuals with severe claustrophobia and/or conned space anxiety -Individuals with certain communication disorders
-Patients with other anatomical abnormalities
-Patients with decreased neck mobility due to arthritis or other causes

SET UP OF DEVICE: See next page for setup instructions.

USAGE: See SOP for use instructions. This device intended for use on one patient. Dispose after use. Not intended for re-use.

BODY CONTACTING MATERIALS:
+Thermoplastic Polyurethane (TPU)
+ Polyethylene Terephthalate Glycol-modied (PETG)
+ Low Density Polyethylene (LDPE)

CLEANING: If cleaning unit before use is required for any reason an isopropanol based cleaner is recommended as other cleaning agents may damage TPU or other plastics on device. This product is intended for use on a single patient and should not be reused.

REMOVAL OF DEVICE: If device impedes care of or communication with patient it should be removed immediately. To remove follow these steps:

1) Unhook cords from both sides of the device (four hooks total)
2) Lift front drape to avoid covering patient’s face
3) Slide device out from beneath patients head, gently lifting patients head if necessary.

# Apollo 4

## PRIOR TO USE: LABELS AND PRECAUTIONS

### Negative Pressure Isolation Hood

2/4

### 46 Cottage Street, Watertown, MA, 02472

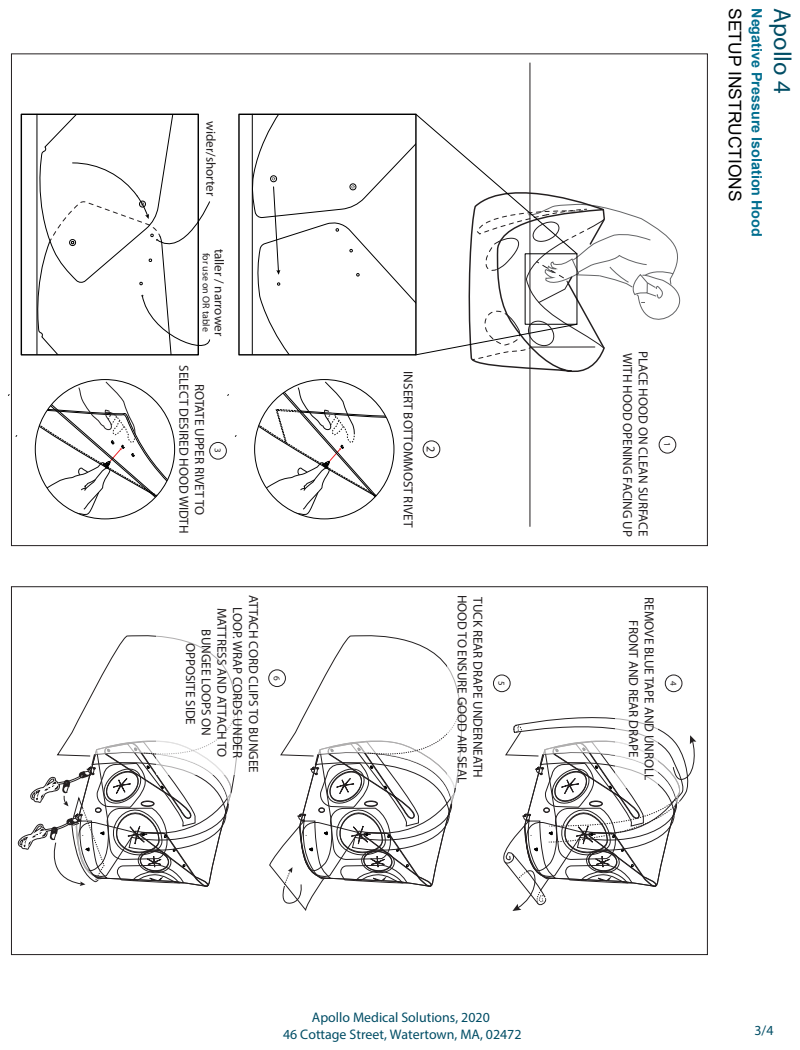
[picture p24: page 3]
OPPOSITE SIDE; SETUP INSTRUCTIONS; Apollo 4

Negative Pressure Isolation Hood

wider/shorter taller / narrower for use on OR table 3

WITH HOOD OPENING FACING UP

PLACE HOOD ON CLEAN SURFACE

SELECT DESIRED HOOD WIDTH

INSERT BOTTOMMOST RIVET

ROTATE UPPER RIVET TO

ATTACH CORD CLIPS TO BUNGEE

HOOD TO ENSURE GOOD AIR SEAL

TUCK REAR DRAPE UNDERNEATH

REMOVE BLUE TAPE AND UNROLL

MATTRESS AND ATTACH TO

LOOP. WRAP CORDS UNDER

FRONT AND REAR DRAPE

BUNGEE LOOPS ON

1. SETUP and USE
- Place patient in hood
- Place procedure instruments in hood (e.g., intubating equipment, ventilator tubing, etc.) through the FRONT of the hood under drape- do NOT attempt to place them though the arm ports as this can restrict movement needed for intubation. At no time should indwelling patient lines be put through arm ports as this could hinder emergency removal safely.
- Lower drape to enclose space, tuck drape in around patient’s body, place blanket over chest and drape edge to help seal chamber as much as possible. Some minor entrainment of room air is expected.
- Turn on suction prior to beginning aerosolizing procedure (see table below for which suction is acceptable)
- Perform procedure- (e.g. intubation, initiate CPAP, etc.). Emergency note: Health Care Provider (HCP) can pull drape up or remove entire hood immediately in case of hood impairs care or communication. Remember, the hood is not intended to replace proper PPE.
- For temporary aerosolizing procedures (intubation, extubation, etc.) leave drape down for 12 minutes (single wall suction line) or 2 minutes (DESCRIPTION OF EVACUATOR HERE), see chart below.
- If aerosolizing procedure is ongoing (eg, CPAP, HFNC, etc) then EVACUATOR suction must be used continuously, other than during brief transport. If suction is o for any reason, or drape must be raised, aerosol protection will decrease signicantly. In this scenario HCP may consider non-aerosolizing oxygen source if clinically acceptable option is available.
- Disposal: ensure hood is NOT returned to stock rooms for re-use. Single patient use only. Apollo hood and all parts are fully dispos-able. If hood is temporarily removed from patient, it is to be placed in a non-contact area, o the oor and within the patient room while awaiting re-application for use on the same patient at a later time.

Wall Suction at Max
(40L/min)

Bu alo suction set at
80% power | Comments
Intubation / extubation | Bu alo suction preferred
TEE or EGD (intubated) | Bu alo suction preferred
Nebulizer treatment | Bu alo suction preferred
Bronchoscopy / BAL | Bu alo suction preferred
CPAP/BIPAP | Bu alo suction 80% required
HFNC | Bu alo suction 80% required

Suggested suction choice

# Apollo 4

## STANDARD OPERATING PROCEDURE

### Negative Pressure Isolation Hood

4/4

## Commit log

2020-05-04 assembly instructions update
2020-05-05 Create 2020_05_04 Apollo3_Cut.dxf
    [2020_05_04 Apollo3_Cut.dxf]
2020-05-05 Updates PrintReady PDF
2020-05-05 Added ArmPort Detail to CutFile
    [2020_05_04 Apollo3_Cut.dxf, 2020_05_05 Apollo3_Cut File.dxf]
2021-08-30 Add files via upload
    Apollo 3 Production Model which was purchased and tested by MGH. Main difference from previous models being the modified shape of the main body to allow for two units to be flat cut from a single 4' 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
    [apollo3_productionModel_BOM.xlsx, apollo3_productionModel_mainBody_twoPer4x8Sheet.dxf]

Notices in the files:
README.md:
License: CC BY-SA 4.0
